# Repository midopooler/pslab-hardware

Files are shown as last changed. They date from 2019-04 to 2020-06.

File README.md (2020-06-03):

# PSLab Hardware

Hardware development and schematics repository for the [Pocket Science Lab (PSLab)](https://pslab.io) open-hardware platform.






The goal of Pocket Science Lab is to create an Open Source hardware device (open on all layers) and software applications that can be used for experiments by teachers, students and scientists. Our tiny pocket lab provides an array of instruments for doing science and engineering experiments. It provides functions of numerous measurement tools including an oscilloscope, a waveform generator, a frequency counter, a programmable voltage, current source and even a component to control robots with up to four servos. Our website is at https://pslab.io. The first version of the hardware (v1) was developed by [Jithin B P](https://pslab.io/team/). Later versions were developed by [Padmal](https://github.com/CloudyPadmal).

Front Side                        | Back Side
 -------------------------------- | ----------------------------------
 | 

Please find the pin-out diagram of the PSLab v5 [here](docs/pin_layouts/PSLab_Pin_Layout.pdf).

## Applications and Firmware Source Repositories

| (https://github.com/fossasia/pslab-firmware)	|(https://f-droid.org/en/packages/io.pslab/)	| (https://play.google.com/store/apps/details?id=io.pslab)	| (https://github.com/fossasia/pslab-desktop/tree/install)	| (https://github.com/fossasia/pslab-desktop/tree/install)	|
|---	|---	|---	|---	|---	|

The following software components are available:
* Firmware: https://github.com/fossasia/pslab-firmware
* Android app: https://github.com/fossasia/pslab-android
* Desktop app: https://github.com/fossasia/pslab-desktop

## Buy Device

* You can get a Pocket Science Lab device from the [FOSSASIA Shop](https://fossasia.com).
* More resellers are listed on the [PSLab website](https://pslab.io/shop/).

## Communication

* The PSLab [chat channel is on Gitter](https://gitter.im/fossasia/pslab).
* Please also join us on the [PSLab Mailing List](https://groups.google.com/forum/#!forum/pslab-fossasia).

## Content of Repository

* **/archives**: Contains previous versions of PSLab schematics
* **/docs**: Supplement materials, schematics as PDFs, images of PSLab
* **/schematics**: PCB layout of PSLab device

## Hardware Specifications

* 4-Channel up to 2MSPS Oscilloscope with software selectable amplification stages.
* 12-bit Voltmeter with programmable gain. Input ranges from +/-10 mV to +/-16 V
* 3x 12-bit Programmable voltage sources +/-3.3 V,+/-5V,0-3 V
* 12-bit Programmable current source. 0-3.3 mA
* Supports Advanced Plugins/Add-on Modules
* 4-Channel, 4 MHz, Logic Analyzer
* 2x Sine/Triangular wave generators. 5 Hz to 5 kHz. Manual amplitude control for SI1
* 4x PWM generators. 15 nS resolution. Up to 8 MHz
* Capacitance Measurement. pF to uF range
* I2C, SPI, UART data buses for Accelerometer, Gyroscope, humidity, temperature modules etc.

## Development Platform

* Microcontroller Platform: [PIC24EP256GP204](http://www.microchip.com/wwwproducts/en/PIC24EP256GP204)
* IDE: [MPLABX IDE v3.35](http://www.microchip.com/mplab/mplab-x-ide) (Supported on Linux/Windows/Mac)
* Compiler: [MPLAB® XC16 Compiler](http://www.microchip.com/mplab/compilers)
* Programming Tool: [PICkit™ 3 In-Circuit Debugger](http://www.microchip.com/Developmenttools/ProductDetails.aspx?PartNO=PG164130)

## Features

### Oscilloscope

One of the main features of PSLab is the 4-channel Oscilloscope which can monitor analog inputs at a maximum of 2 million samples per second. It includes controls such as triggering and gain selection. Uses Python-Scipy for curve fitting.

### Waveform Generator

* SI1: 5 Hz – 5 kHz arbitrary waveform generator. Manual amplitude control up to +/-3 Volts
* SI2: 5 Hz – 5 kHz arbitrary waveform generator. The amplitude of +/-3 Volts. Attenuable via software
* SQx: There are four phases correlated PWM outputs with maximum frequency 32 MHz, 15 nanosecond duty cycle, and phase difference control.

### Measurement Functions

* Frequency counter tested up to 16 MHz.
* Capacitance Measurement. pF to uF range
* PSLab has several 12-bit analog inputs (function as voltmeters) with programmable gains, and maximum ranges varying from +/-5 mV to +/-16 V.

### Voltage and Current Source

* 12-bit Constant Current source. Maximum current 3.3 mA (subject to load resistance).
* PSLab has three 12-bit Programmable voltage sources +/-3.3 V,+/-5 V,0-3 V. (PV1, PV2, PV3) controls

### Other Useful Tools

* 4MHz, 4-channel Logic analyzer with 15 nS resolution.Voltage and Current Sources
* SPI, I2C, UART outputs
* Graphical Interfaces for Oscilloscope, Logic Analyser, streaming data, wireless acquisition and several experiments developed that use a common framework which drastically reduces code required to incorporate control and plotting widgets.
* PSLab also has space for an ESP-12 module for WiFi access with access point/ station mode.

### Advanced Controls
* Advanced Controls with Oscilloscope
* Data Logger
* Logic Analyzer
* Wireless Sensors (Work in progress…)

## Parts List

* [PIC24EP256GP204](http://www.microchip.com/wwwproducts/en/PIC24EP256GP204) - Main uC
* [MCP6S21](http://www.microchip.com/wwwproducts/en/mcp6s21) - Programmable Gain Amplifier
* [MCP4728](http://www.microchip.com/wwwproducts/en/mcp4728) - 4 channel DAC
* [TC7660](http://www.microchip.com/wwwproducts/en/TC7660) - Charge Pump voltage invertor
* [TC1240A](http://www.microchip.com/wwwproducts/en/TC1240A) - Charge Pump voltage doubler
* [TL082](http://www.ti.com/product/TL082) - 2 channel Op-Amp
* [LM324](http://www.ti.com/product/LM324) - 4 channel Op-Amp
* [LM1117](http://www.ti.com/product/LM1117) - 3.3 V regulator
* [MCP2200](http://www.microchip.com/wwwproducts/en/MCP2200) - USB-UART Bridge
* [74HC126](http://www.ti.com/product/SN74HC126) - 4 channel Buffer
* 0.5 A Fuse
* Assorted resistors, capacitors & diodes
* Optional Parts: Extension slots to solder ESP and Bluetooth components to the device are available.
  * [ESP8266 (ESP-12E)](https://www.adafruit.com/product/2491) - UART-TCP bridge
  * Bluetooth

## Version Information

| Version | Content | Image |
| -------------- | ------- | ------- |
| PSLab KiCAD v1   | Original version with `SEELABLET` schematics and layout files |  |
| PSLab KiCAD v2 | Developed version with new additions (Voltage regulator, Oscillator) |  |
| PSLab KiCAD v3 | Device layout changed to Arduino Uno form factor |  |
| PSLab KiCAD v4 | Assembly optimized version with Arduino Mega form factor having components mounted only on top side |  |
| PSLab KiCAD v5 | Added socket for external bluetooth module and bottom silk screen with pin description |  |

## Block Diagram

The following block diagram shows the flow and functions of the hardware and firmware.



## Casing

A lasercut casing design for the Pocket Science Lab is available at https://github.com/fossasia/pslab-case.

## License

This project is Free and Open Source software. The project is licensed under the [Apache License v2](LICENSE). Copyright is owned by FOSSASIA and its contributors. Please refer to the license files for more details.

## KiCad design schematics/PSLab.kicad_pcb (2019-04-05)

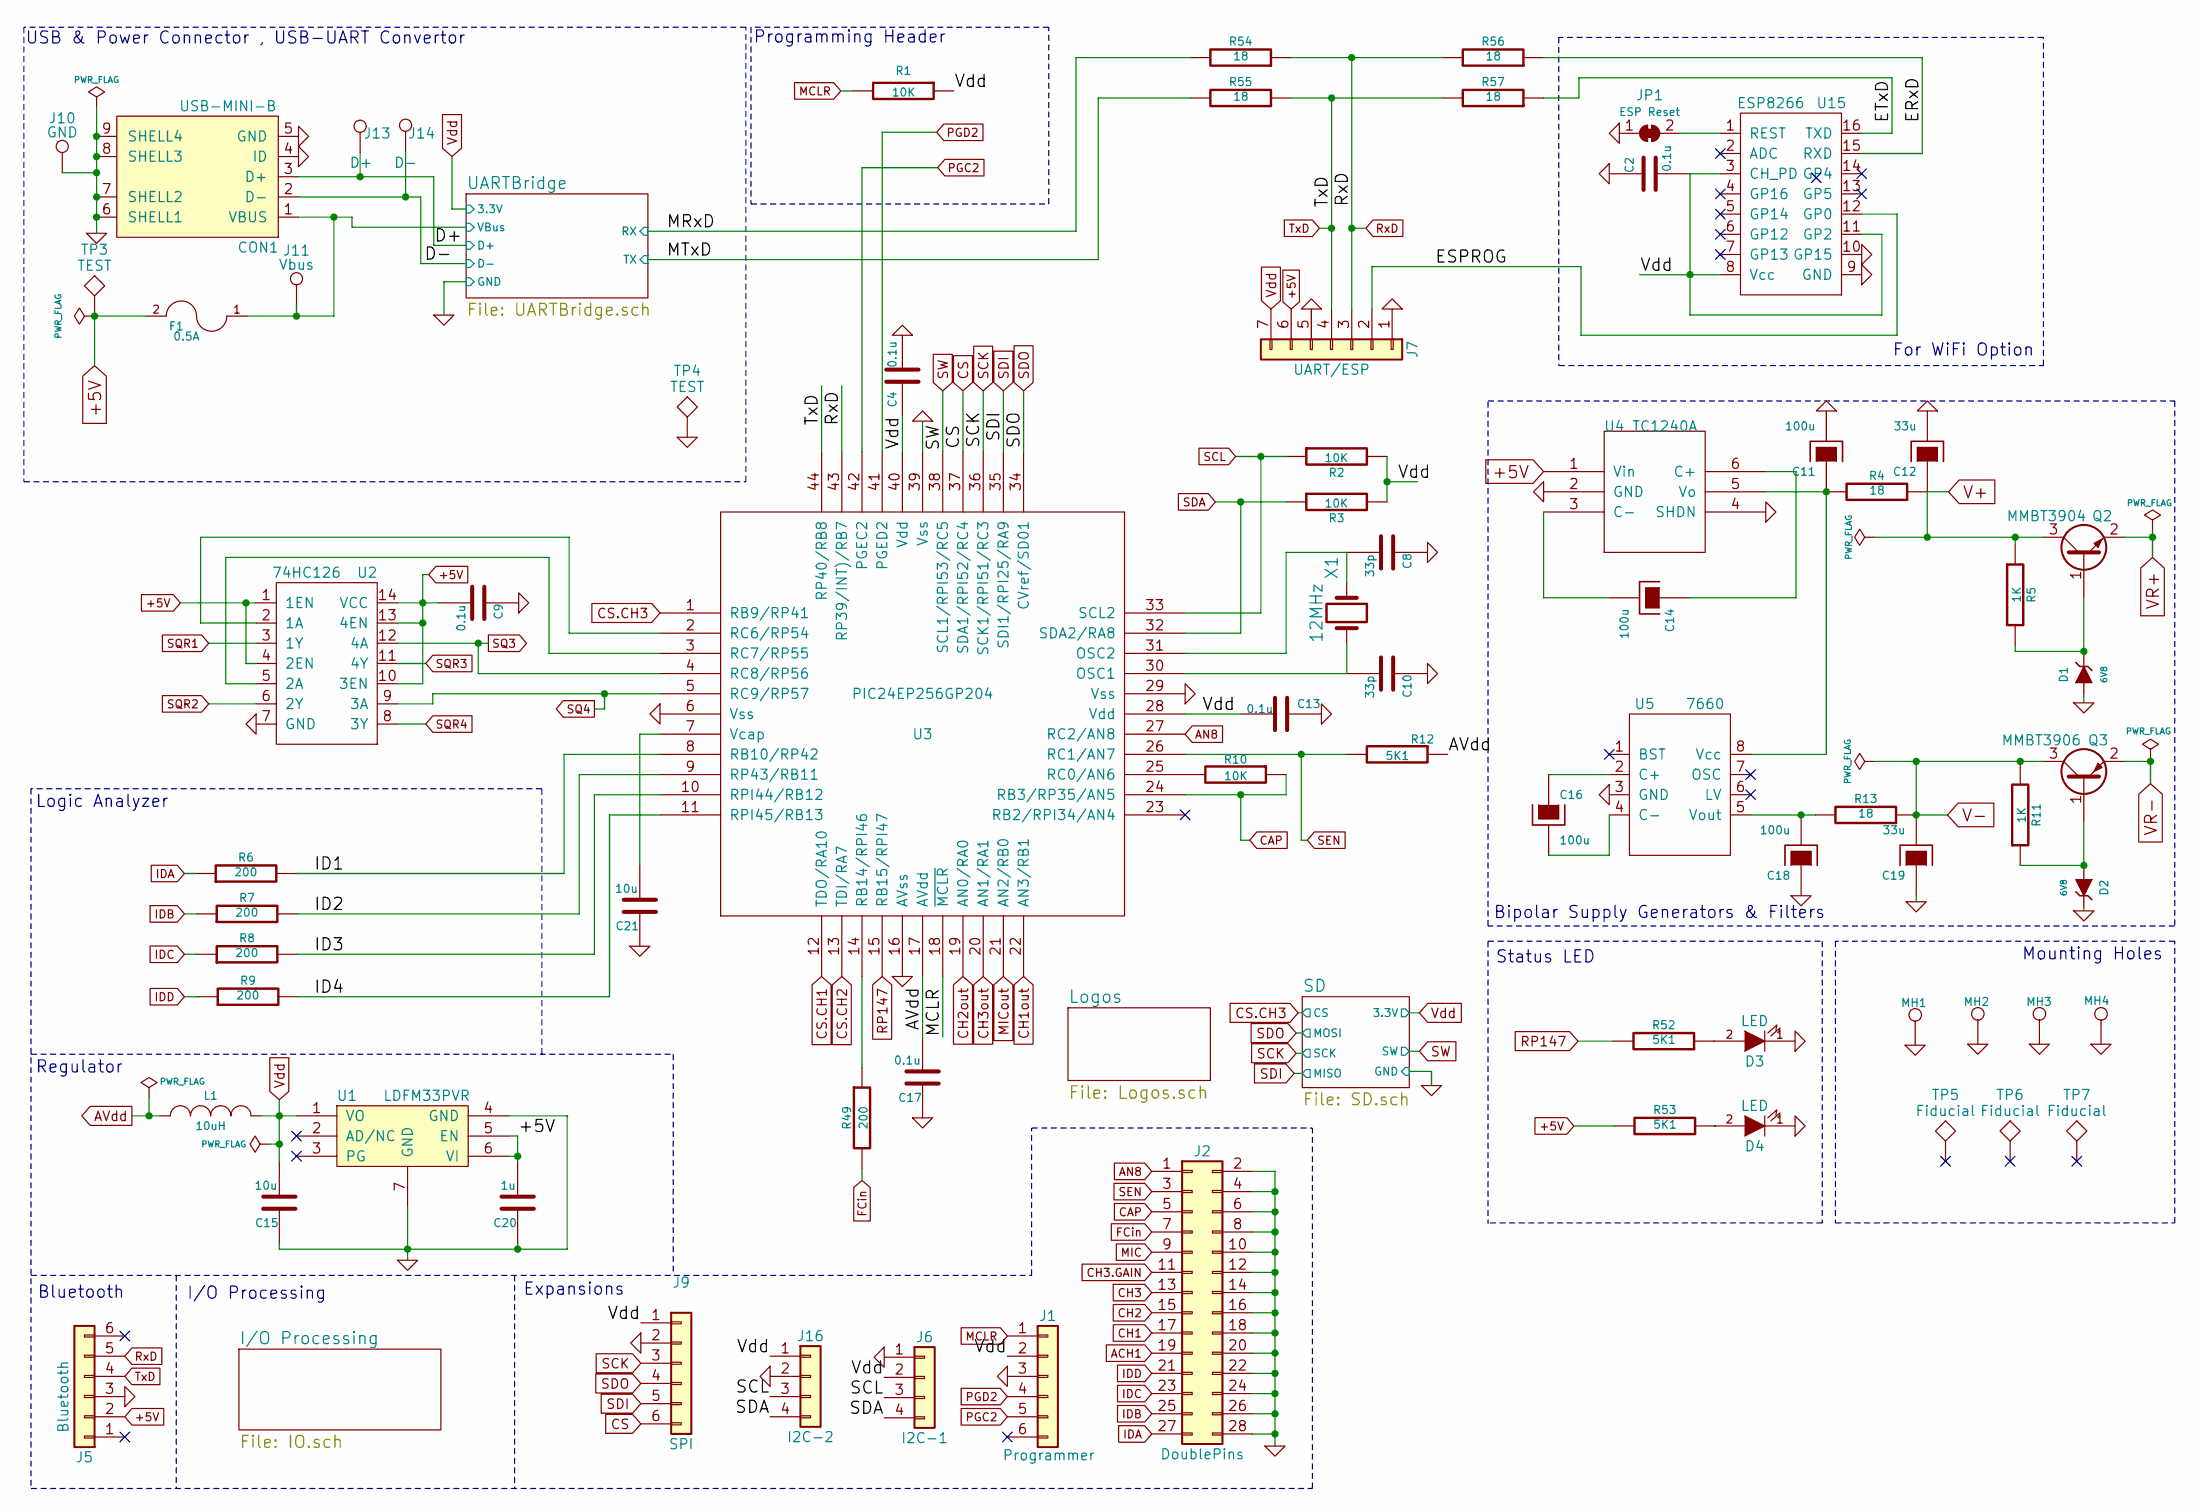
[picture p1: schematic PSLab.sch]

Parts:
C2, C4, C9, C13, C17: 0.1u; C_0603
C8, C10: 33p; C_0603
C11, C14, C16, C18: 100u; CP_Tantalum_Case-C_EIA-6032-28_Reflow
C12, C19: 33u; CP_Tantalum_Case-B_EIA-3528-21_Reflow
C15, C21: 10u; C_0603
C20: 1u; C_0603
CON1: USB-MINI-B; USB_Micro-B
D1, D2: 6V8; D_MiniMELF
D3, D4: LED; LED_0805
F1: 0.5A; Fuse_SMD1206_Reflow
J1: Programmer; Pin_Header_Straight_1x06_Pitch2.54mm
J2: DoublePins; Pin_Header_Straight_2x14_Pitch2.54mm
J5: Bluetooth; Pin_Header_Straight_1x06_Pitch2.54mm
J6: I2C-1; Pin_Header_Straight_1x04_Pitch2.54mm
J7: UART/ESP; Pin_Header_Straight_1x07_Pitch2.54mm
J9: SPI; Pin_Header_Straight_1x06_Pitch2.54mm
J10: GND; Measurement_Point_Square-SMD-Pad_Small
J11: Vbus; Measurement_Point_Square-SMD-Pad_Small
J13: D+; Measurement_Point_Square-SMD-Pad_Small
J14: D-; Measurement_Point_Square-SMD-Pad_Small
J16: I2C-2; Pin_Header_Straight_1x04_Pitch2.54mm
JP1: ESP Reset; GS2
L1: 10uH; L_0603
MH1, MH2, MH3, MH4: M; MountingHole_3.2mm_M3_DIN965_Pad
Q2: MMBT3904; SOT-23
Q3: MMBT3906; SOT-23
R1, R2, R3, R10: 10K; R_0603
R4, R13, R54, R55, R56, R57: 18; R_0603
R5, R11: 1K; R_0603
R6, R7, R8, R9, R49: 200; R_0603
R12, R52, R53: 5K1; R_0603
TP3, TP4: TEST; Measurement_Point_Round-SMD-Pad_Small
TP5, TP6, TP7: Fiducial; Fiducial_0.5mm_Dia_1mm_Outer
U1: LDFM33PVR; DFN-6-1EP_3x3mm_Pitch0.95mm
U2: 74HC126; SOIC-14_3.9x8.7mm_Pitch1.27mm
U3: PIC24EP256GP204; TQFP-44_10x10mm_Pitch0.8mm
U4: TC1240A; SOT-23-6
U5: 7660; SOIC-8_3.9x4.9mm_Pitch1.27mm
U15: ESP8266; Hopref_RFM9XW_SMD
X1: 12MHz; Crystal_SMD_5032-2pin_5.0x3.2mm

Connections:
3.3V: C2.2, C4.1, C13.2, C15.2, J1.2, J6.2, J7.7, J9.1, J16.1, L1.2, R1.1, R2.2, R3.2, U1.1 (VO), U3.28 (Vdd), U3.40 (Vdd), U15.3 (CH_PD), U15.8 (Vcc), U15.11 (GP2); also elsewhere on the board
+5V: C9.2, C20.2, F1.2, J5.2, J7.6, R53.2, TP3.1, U1.5 (EN), U1.6 (VI), U2.1 (1EN), U2.4 (2EN), U2.10 (3EN), U2.13 (4EN), U2.14 (VCC), U4.1 (Vin); also elsewhere on the board
/ERxD: R56.1, U15.15 (RXD)
/ESPROG: J7.2, U15.12 (GP0)
/ETxD: R57.1, U15.16 (TXD)
/ID1: R6.2, U3.8 (RB10/RP42)
/ID2: R7.2, U3.9 (RP43/RB11)
/ID3: R8.2, U3.10 (RPI44/RB12)
/ID4: R9.2, U3.11 (RPI45/RB13)
/MRxD: R54.2; also elsewhere on the board
/MTxD: R55.2; also elsewhere on the board
ACH1: J2.19; also elsewhere on the board
AN8: J2.1, U3.27 (RC2/AN8)
AVdd: C17.2, L1.1, R12.1, U3.17 (AVdd); also elsewhere on the board
CAP: J2.5, R10.1, U3.24 (RB3/RP35/AN5)
CH1: J2.17; also elsewhere on the board
CH1out: U3.22 (AN3/RB1); also elsewhere on the board
CH2: J2.15; also elsewhere on the board
CH2out: U3.19 (AN0/RA0); also elsewhere on the board
CH3: J2.13; also elsewhere on the board
CH3.GAIN: J2.11; also elsewhere on the board
CH3out: U3.20 (AN1/RA1); also elsewhere on the board
CS: J9.6, U3.37 (SDA1/RPI52/RC4)
CS.CH1: U3.12 (TDO/RA10); also elsewhere on the board
CS.CH2: U3.13 (TDI/RA7); also elsewhere on the board
CS.CH3: U3.1 (RB9/RP41); also elsewhere on the board
D+: CON1.3 (D+), J13.1; also elsewhere on the board
D-: CON1.2 (D-), J14.1; also elsewhere on the board
FCin: J2.7, R49.2
GND: C2.1, C4.2, C8.1, C9.1, C10.1, C11.2, C12.2, C13.1, C15.1, C17.1, C18.1, C19.1, C20.1, C21.1, CON1.4 (ID), CON1.5 (GND), CON1.6 (SHELL1), CON1.7 (SHELL2), CON1.8 (SHELL3), CON1.9 (SHELL4), D1.1 (A), D2.2 (K), D3.1 (K), D4.1 (K), J1.3, J2.2, J2.4, J2.6, J2.8, J2.10, J2.12, J2.14, J2.16, J2.18, J2.20, J2.22, J2.24, J2.26, J2.28, J5.3, J6.1, J7.1, J7.5, J9.2, J10.1, J16.2, JP1.1 (A), MH1.1, MH2.1, MH3.1, MH4.1, TP4.1, U1.4 (GND), U1.7 (GND), U2.7 (GND), U3.6 (Vss), U3.16 (AVss), U3.29 (Vss), U3.39 (Vss), U4.2 (GND), U4.4 (SHDN), U5.3 (GND), U15.9 (GND), U15.10 (GP15); also elsewhere on the board
IDA: J2.27, R6.1
IDB: J2.25, R7.1
IDC: J2.23, R8.1
IDD: J2.21, R9.1
MCLR: J1.1, R1.2, U3.18 (~MCLR)
MIC: J2.9; also elsewhere on the board
MICout: U3.21 (AN2/RB0); also elsewhere on the board
unnamed: C8.2, U3.31 (OSC2), X1.1
unnamed: C10.2, U3.30 (OSC1), X1.2
unnamed: C11.1, R4.2, U4.5 (Vo), U5.8 (Vcc)
unnamed: C14.1, U4.6 (C+)
unnamed: C14.2, U4.3 (C-)
unnamed: C16.1, U5.2 (C+)
unnamed: C16.2, U5.4 (C-)
unnamed: C18.2, R13.2, U5.5 (Vout)
unnamed: C21.2, U3.7 (Vcap)
unnamed: D1.2 (K), Q2.1 (B), R5.2
unnamed: D2.1 (A), Q3.1 (B), R11.1
unnamed: D3.2 (A), R52.1
unnamed: D4.2 (A), R53.1
unnamed: JP1.2 (B), U15.1 (REST)
unnamed: R10.2, U3.25 (RC0/AN6)
unnamed: R49.1, U3.14 (RB14/RPI46)
unnamed: U2.2 (1A), U3.2 (RC6/RP54)
unnamed: U2.5 (2A), U3.3 (RC7/RP55)
PGC2: J1.5, U3.42 (PGEC2)
PGD2: J1.4, U3.41 (PGED2)
RP147: R52.2, U3.15 (RB15/RPI47)
RxD: J5.5, J7.3, R54.1, R56.2, U3.43 (RP39/INT)/RB7)
SCK: J9.3, U3.36 (SCK1/RPI51/RC3); also elsewhere on the board
SCL: J6.3, J16.3, R2.1, U3.33 (SCL2); also elsewhere on the board
SDA: J6.4, J16.4, R3.1, U3.32 (SDA2/RA8); also elsewhere on the board
SDI: J9.5, U3.35 (SDI1/RPI25/RA9); also elsewhere on the board
SDO: J9.4, U3.34 (CVref/SD01); also elsewhere on the board
SEN: J2.3, R12.2, U3.26 (RC1/AN7)
SQ3: U2.12 (4A), U3.4 (RC8/RP56); also elsewhere on the board
SQ4: U2.9 (3A), U3.5 (RC9/RP57); also elsewhere on the board
SQR1: U2.3 (1Y); also elsewhere on the board
SQR2: U2.6 (2Y); also elsewhere on the board
SQR3: U2.11 (4Y); also elsewhere on the board
SQR4: U2.8 (3Y); also elsewhere on the board
SW: U3.38 (SCL1/RPI53/RC5); also elsewhere on the board
TxD: J5.4, J7.4, R55.1, R57.2, U3.44 (RP40/RB8)
V+: C12.1, Q2.3 (C), R4.1, R5.1; also elsewhere on the board
V-: C19.2, Q3.3 (C), R11.2, R13.1; also elsewhere on the board
VBus: CON1.1 (VBUS), F1.1, J11.1; also elsewhere on the board
VR+: Q2.2 (E); also elsewhere on the board
VR-: Q3.2 (E); also elsewhere on the board

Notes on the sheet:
For WiFi Option
USB & Power Connector , USB-UART Convertor
Programming Header
Bipolar Supply Generators & Filters
Status LED
Mounting Holes
Expansions
I/O Processing
Regulator
Logic Analyzer
Bluetooth

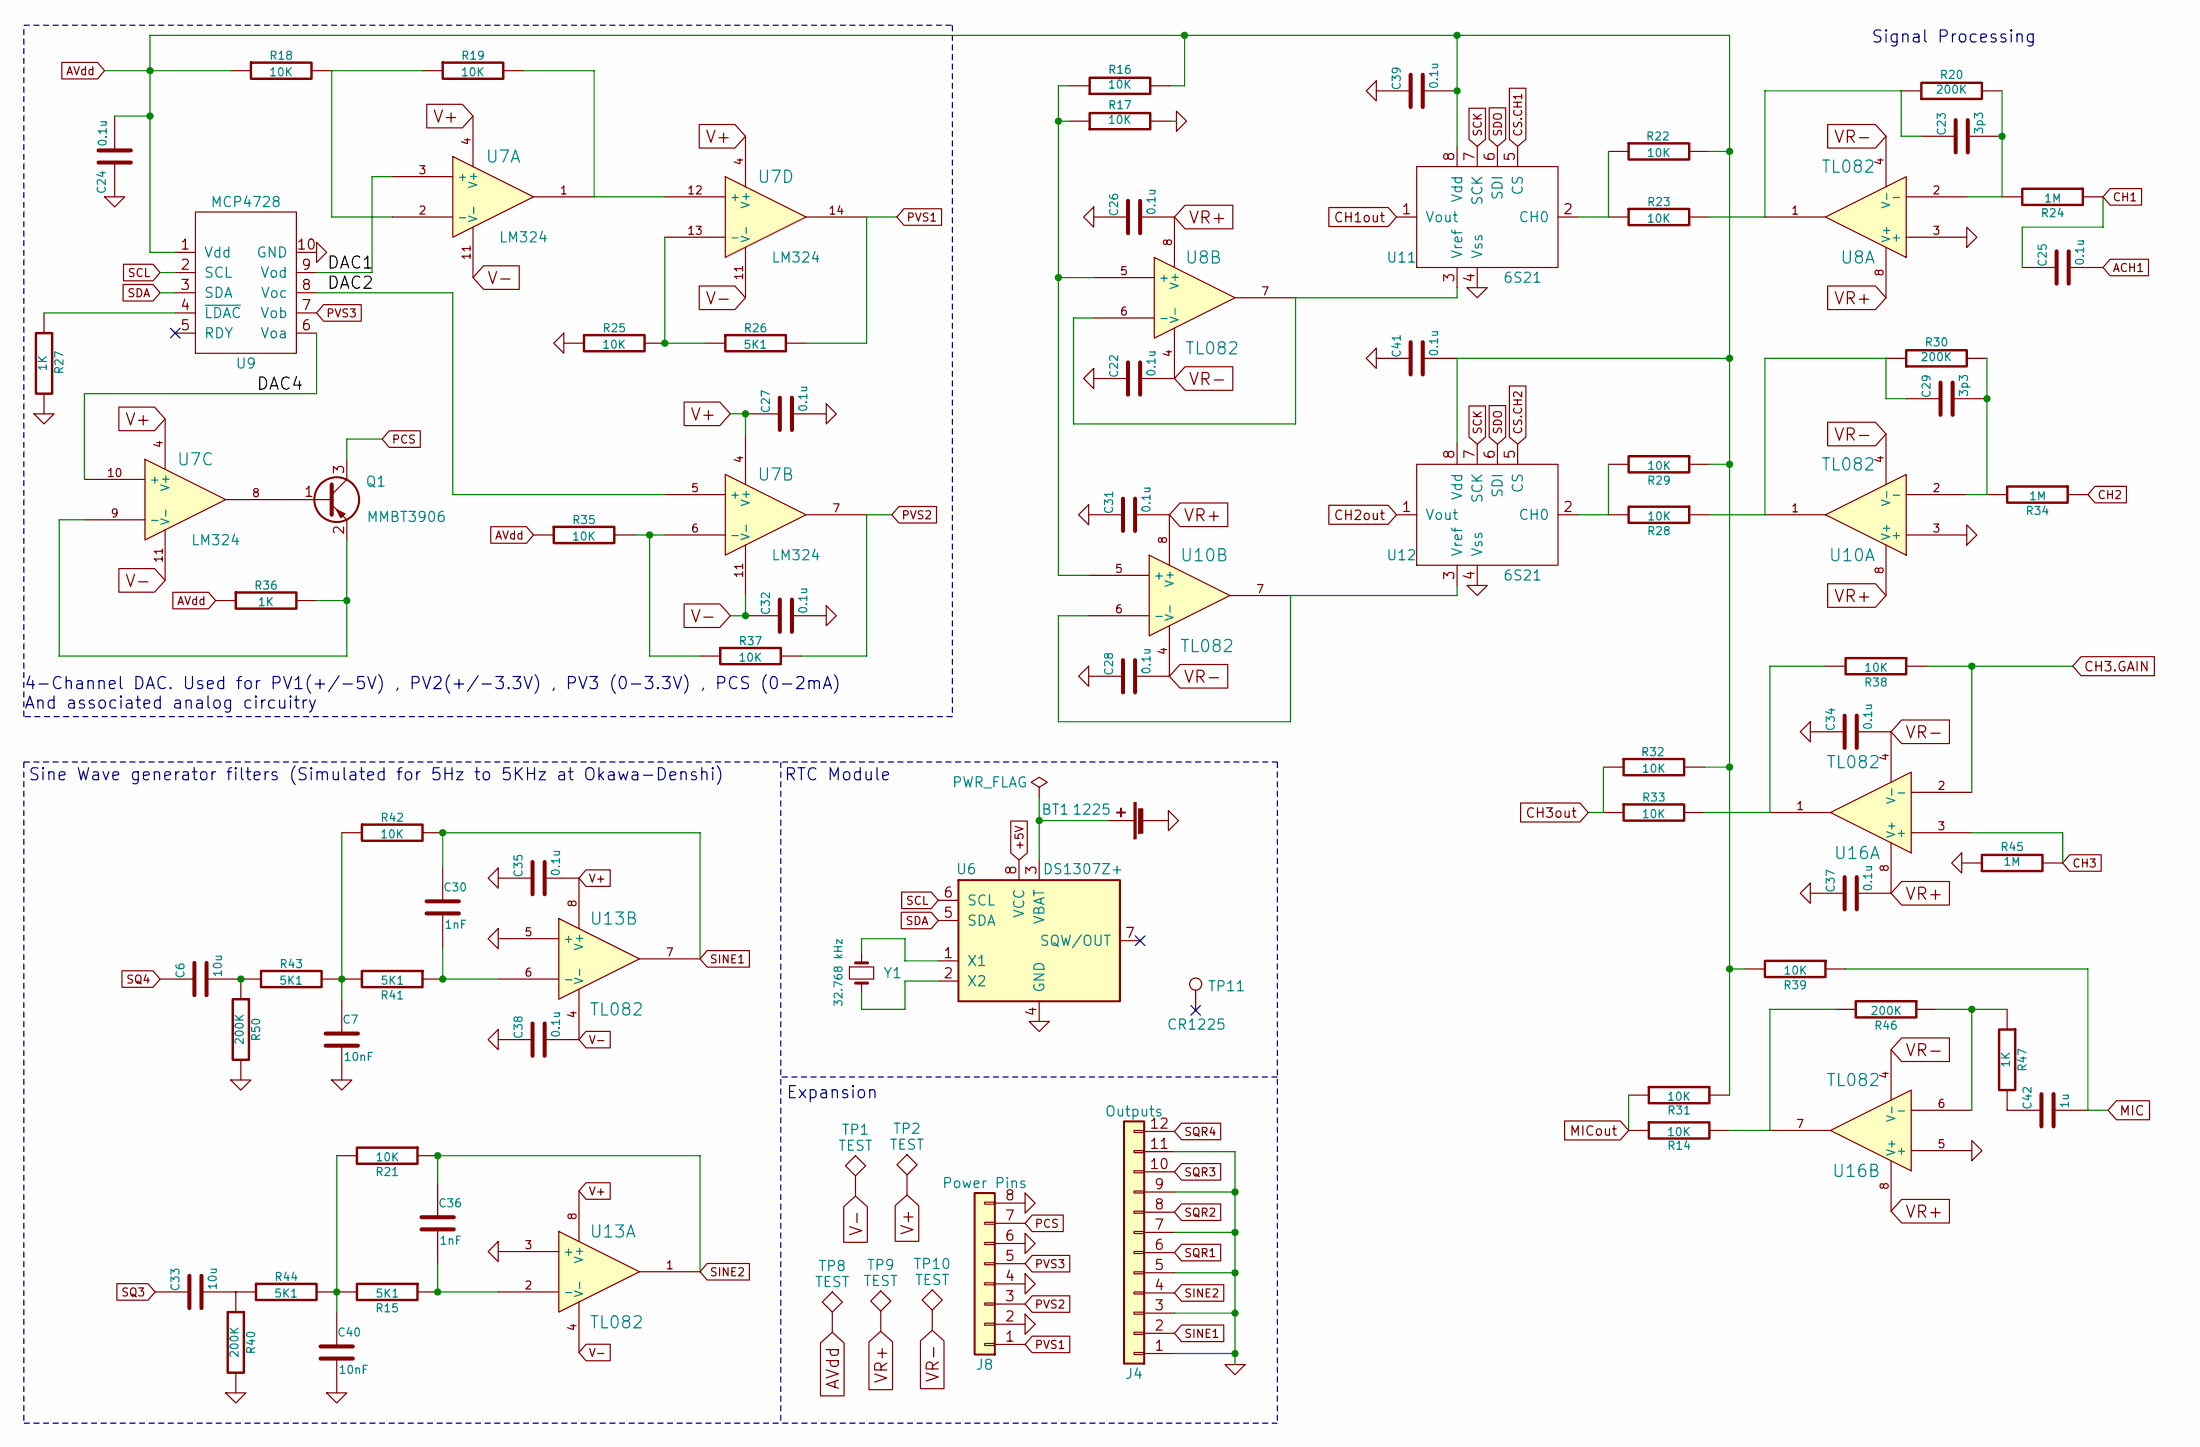
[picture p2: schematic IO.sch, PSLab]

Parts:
BT1: 1225; BatteryHolder_LINX_BAT-HLD-012-SMT
C6, C33: 10u; C_0603
C7, C40: 10nF; C_0603
C22, C24, C25, C26, C27, C28, C31, C32, C34, C35, C37, C38, C39, C41: 0.1u; C_0603
C23, C29: 3p3; C_0603
C30, C36: 1nF; C_0603
C43: 1u; C_0603
J4: Outputs; Pin_Header_Straight_1x12_Pitch2.54mm
J8: Power Pins; Pin_Header_Straight_1x08_Pitch2.54mm
Q1: MMBT3906; SOT-23
R14, R16, R17, R18, R19, R21, R22, R23, R25, R28, R29, R31, R32, R33, R35, R37, R38, R39, R42: 10K; R_0603
R15, R26, R41, R43, R44: 5K1; R_0603
R20, R30, R40, R46, R50: 200K; R_0603
R24, R34, R45: 1M; R_0603
R27, R36, R47: 1K; R_0603
TP1, TP2, TP8, TP9, TP10: TEST; Measurement_Point_Round-SMD-Pad_Small
TP11: CR1225; Battery_CR1225
U6: DS1307Z+; SOIC-8_3.9x4.9mm_P1.27mm
U7: LM324; SOIC-14_3.9x8.7mm_Pitch1.27mm
U8, U10, U13, U16: TL082; SOIC-8_3.9x4.9mm_Pitch1.27mm
U9: MCP4728; MSOP-10_3x3mm_Pitch0.5mm
U11, U12: 6S21; SOIC-8_3.9x4.9mm_Pitch1.27mm
Y1: 32.768 kHz; Crystal_SMD_3215-2Pin_3.2x1.5mm

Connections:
+5V: U6.8 (VCC); also elsewhere on the board
/I/O Processing/DAC1: U7.3 (+), U9.9 (Vod)
/I/O Processing/DAC2: U7.5 (+), U9.8 (Voc)
/I/O Processing/DAC4: U7.10 (+), U9.6 (Voa)
ACH1: C25.2; also elsewhere on the board
AVdd: C24.2, C39.2, C41.2, R16.2, R18.1, R22.2, R29.1, R31.2, R32.2, R35.1, R36.1, R39.2, TP8.1, U9.1 (Vdd), U11.8 (Vdd), U12.8 (Vdd); also elsewhere on the board
CH1: C25.1, R24.1; also elsewhere on the board
CH1out: U11.1 (Vout); also elsewhere on the board
CH2: R34.1; also elsewhere on the board
CH2out: U12.1 (Vout); also elsewhere on the board
CH3: R45.2, U16.3 (+); also elsewhere on the board
CH3.GAIN: R38.1, U16.2 (-); also elsewhere on the board
CH3out: R32.1, R33.1; also elsewhere on the board
CS.CH1: U11.5 (CS); also elsewhere on the board
CS.CH2: U12.5 (CS); also elsewhere on the board
GND: BT1.2 (-), C7.2, C22.1, C24.1, C26.1, C27.2, C28.1, C31.1, C32.2, C34.1, C35.1, C37.1, C38.1, C39.1, C40.2, C41.1, J4.1, J4.3, J4.5, J4.7, J4.9, J4.11, J8.2, J8.4, J8.6, J8.8, R17.2, R25.1, R27.2, R40.2, R45.1, R50.2, U6.4 (GND), U8.3 (+), U9.10 (GND), U10.3 (+), U11.4 (Vss), U12.4 (Vss), U13.3 (+), U13.5 (+), U16.5 (+); also elsewhere on the board
MIC: R39.1; also elsewhere on the board
MICout: R14.1, R31.1; also elsewhere on the board
unnamed: BT1.1 (+), U6.3 (VBAT)
unnamed: C6.2, R43.1, R50.1
unnamed: C7.1, R41.2, R42.1, R43.2
unnamed: C23.1, R20.1, R23.2, U8.1
unnamed: C23.2, R20.2, R24.2, U8.2 (-)
unnamed: C29.1, R28.1, R30.1, U10.1
unnamed: C29.2, R30.2, R34.2, U10.2 (-)
unnamed: C30.2, R41.1, U13.6 (-)
unnamed: C33.2, R40.1, R44.1
unnamed: C36.2, R15.1, U13.2 (-)
unnamed: C40.1, R15.2, R21.2, R44.2
unnamed 61: R47.2; also elsewhere on the board
unnamed: Q1.1 (B), U7.8
unnamed: Q1.2 (E), R36.2, U7.9 (-)
unnamed: R14.2, R46.2, U16.7
unnamed: R16.1, R17.1, U8.5 (+), U10.5 (+)
unnamed: R18.2, R19.1, U7.2 (-)
unnamed: R19.2, U7.1, U7.12 (+)
unnamed: R22.1, R23.1, U11.2 (CH0)
unnamed: R25.2, R26.1, U7.13 (-)
unnamed: R27.1, U9.4 (~LDAC)
unnamed: R28.2, R29.2, U12.2 (CH0)
unnamed: R33.2, R38.2, U16.1
unnamed: R35.2, R37.1, U7.6 (-)
unnamed: R46.1, R47.1, U16.6 (-)
unnamed: U6.1 (X1), Y1.1
unnamed: U6.2 (X2), Y1.2
unnamed: U10.6 (-), U10.7, U12.3 (Vref)
unnamed: U8.6 (-), U8.7, U11.3 (Vref)
PCS: J8.7, Q1.3 (C)
PVS1: J8.1, R26.2, U7.14
PVS2: J8.3, R37.2, U7.7
PVS3: J8.5, U9.7 (Vob)
SCK: U11.7 (SCK), U12.7 (SCK); also elsewhere on the board
SCL: U6.6 (SCL), U9.2 (SCL); also elsewhere on the board
SDA: U6.5 (SDA), U9.3 (SDA); also elsewhere on the board
SDO: U11.6 (SDI), U12.6 (SDI); also elsewhere on the board
SINE1: C30.1, J4.2, R42.2, U13.7
SINE2: C36.1, J4.4, R21.1, U13.1
SQ3: C33.1; also elsewhere on the board
SQ4: C6.1; also elsewhere on the board
SQR1: J4.6; also elsewhere on the board
SQR2: J4.8; also elsewhere on the board
SQR3: J4.10; also elsewhere on the board
SQR4: J4.12; also elsewhere on the board
V+: C27.1, C35.2, TP2.1, U7.4 (V+), U13.8 (V+); also elsewhere on the board
V-: C32.1, C38.2, TP1.1, U7.11 (V-), U13.4 (V-); also elsewhere on the board
VR+: C26.2, C31.2, C37.2, TP9.1, U8.8 (V+), U10.8 (V+), U16.8 (V+); also elsewhere on the board
VR-: C22.2, C28.2, C34.2, TP10.1, U8.4 (V-), U10.4 (V-), U16.4 (V-); also elsewhere on the board

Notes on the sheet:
4-Channel DAC. Used for PV1(+/-5V) , PV2(+/-3.3V) , PV3 (0-3.3V) , PCS (0-2mA) And associated analog circuitry
Sine Wave generator filters (Simulated for 5Hz to 5KHz at Okawa-Denshi)
Signal Processing
Expansion
RTC Module

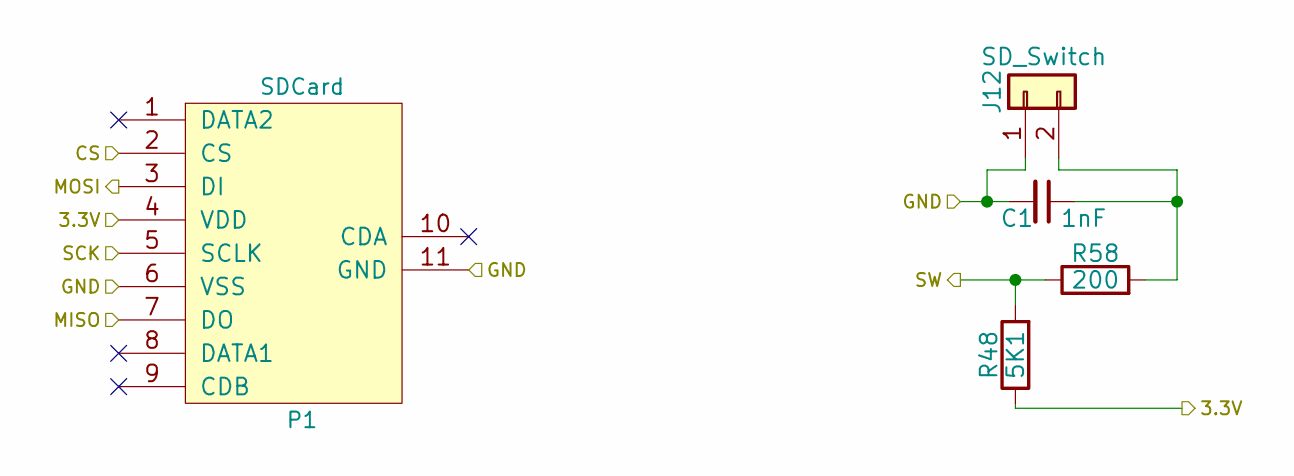
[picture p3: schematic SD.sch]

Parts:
C1: 1nF; C_0603
J12: SD_Switch; SW_SPST_B3U-1000P
P1: SDCard; microSD_HC_Hirose_DM3AT-SF-PEJM5
R48: 5K1; R_0603
R58: 200; R_0603

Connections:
3.3V: P1.4 (VDD), R48.1; also elsewhere on the board
CS.CH3: P1.2 (CS); also elsewhere on the board
GND: C1.2, J12.1, P1.6 (VSS), P1.11 (GND); also elsewhere on the board
unnamed: C1.1, J12.2, R58.2
SCK: P1.5 (SCLK); also elsewhere on the board
SDI: P1.7 (DO); also elsewhere on the board
SDO: P1.3 (DI); also elsewhere on the board
SW: R48.2, R58.1; also elsewhere on the board

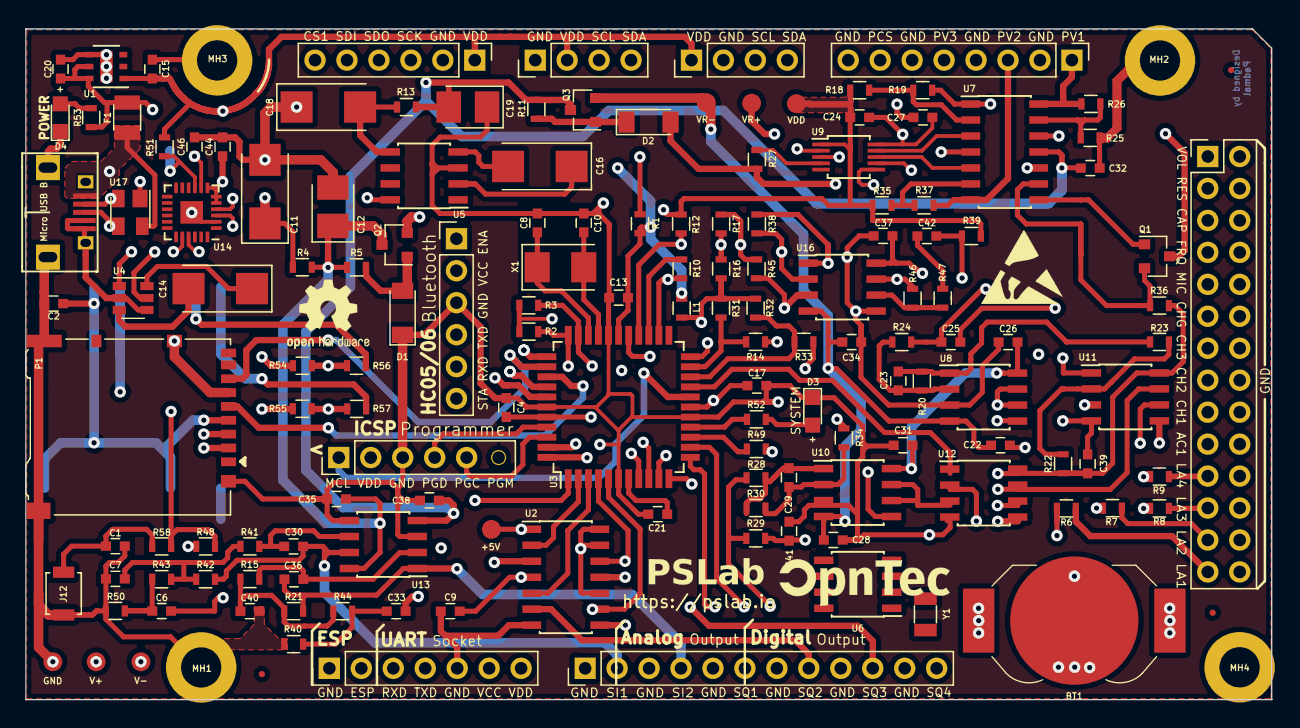
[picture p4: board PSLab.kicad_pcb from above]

Board: 4 copper layers, 99.0 x 53.3 mm, 171 parts (0 on the bottom side), 118 nets.

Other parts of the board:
C42: 1u; C_0603
C44, C46: 4.7u; C_0603
JP2: UART Reset; GS2
R51: 1K; R_0603
S1: OpenHardware; OSHW-Logo2_7.3x6mm_SilkScreen
S2: PSLab_Logo
S3: ESD-Logo; ESD-Logo_6.6x6mm_SilkScreen
S5, S8: OpnTec_Logo
S6: FOSSASIA_Logo_S; FOSSASIA_Logo
S7: PSL_Logo
S9: QR_Code; Website_QR
S10: FOSSASIA_Logo_L; FOSSASIA_LogoL
U14: CP2102; QFN-24-1EP_4x4mm_Pitch0.5mm
U17: SP0503BAHT; SOT-143

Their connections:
3.3V: C44.1, R51.2, U14.5, U14.6, U14.7; also elsewhere on the board
/MRxD: U14.20; also elsewhere on the board
/MTxD: U14.21; also elsewhere on the board
D+: U14.3, U17.3; also elsewhere on the board
D-: U14.4, U17.2; also elsewhere on the board
GND: C44.2, C46.2, JP2.2, U14.2, U14.25, U17.1; also elsewhere on the board
MIC: C42.2; also elsewhere on the board
unnamed 61: C42.1; also elsewhere on the board
unnamed: JP2.1, R51.1, U14.9
VBus: C46.1, U14.8, U17.4; also elsewhere on the board

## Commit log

2019-04-05 feat: added components for RTC
    [IO.sch, PSLab.kicad_pcb, PSLab.sch, SD.sch]
2019-04-05 route: adding missing routes after importing net
    [PSLab.kicad_pcb, PSLab.sch]
2019-04-05 route: rearrange to get more space
    [PSLab.kicad_pcb]
2019-04-05 route: rtc module placement
    [PSLab.kicad_pcb]
